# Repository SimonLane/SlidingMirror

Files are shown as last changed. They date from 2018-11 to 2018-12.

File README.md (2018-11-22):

# Sliding Mirror

For use in alternating between two beams in a microscopy setup. A mirror is moved into position with high reposition accuracy. It has been tested on lasers with path lengths ~4.5m and found to allow better repeatability than for example a ThorLabs flip mirror. It also has the advangtage of optionally being automated.
A translation stage is used to provide the linear translation whilst movement is generated by a servo. A spring couples the servo arm to the stage, allowing the stage to be held tight against one end of its range to ensure the same position every time.

Could also be used to add/remove other components e.g. lenses, from optical path where high positional accuracy is needed.

The design comes in two sizes, based around the 13mm and 25mm translation stages available from ThorLabs. 25mm is easier to set-up and allows space for multiple optical components on the stage, whilst 13mm has a smaller footprint. If using the 13mm, then the 'edgeless' mirror design may be useful.

The designs assume mounting on an optical breadboard with 25mm spacing for M6 bolts.

## Bill of Materials

Part | Number | Product Code | Company | Cost (Aprox. GBP)
---|---|---|---|---
Translation Stage 25mm (or 13mm) | 1 | PT1B/M (MT1B/M) | ThorLabs | 161.42 (167.54)
Mirror mount   | 1   | application specific | -  |  -
M6 screw | 1 pack | SH6MS20 | ThorLabs | 6.66
Servo  | 1 | 781-3058 | RSonline | 11.06
Wires  |  1   | 214-0661 |  RS Online   | 14.29
Switch | 1 | 734-7154 | RS Online | 2.33
USB cable   | 1   | 121-6574   | RS Online  |  2.41
Arduino nano (or similar)  |  1  |  1050-1001-ND | Digi-Key  |  16.66
Spring | 1 pack |  2444377 | Farnell | 6.87
Machine screws | 1 pack | 560-596 | RS Online | 2.39

## Assembly
* Print the 3D part using at least 50% infill
* Remove three of the four servo arms and attach to the servo.
* Attach the servo to the base with M3 screws
* Remove the plug from the servo, then solder the wires to the Arduino Nano as shown in the wiring diagram below
    * Red to 5V*
    * Black to Ground
    * Yellow to any PWM (pin D3,5,6,9,10 or 11)
    * Switch wire one to Ground
    * Switch wire two to Digital pin e.g. D4
**The servo can draw 140mA, which is comfortably handled by the arduino and the USB supply from a computer*
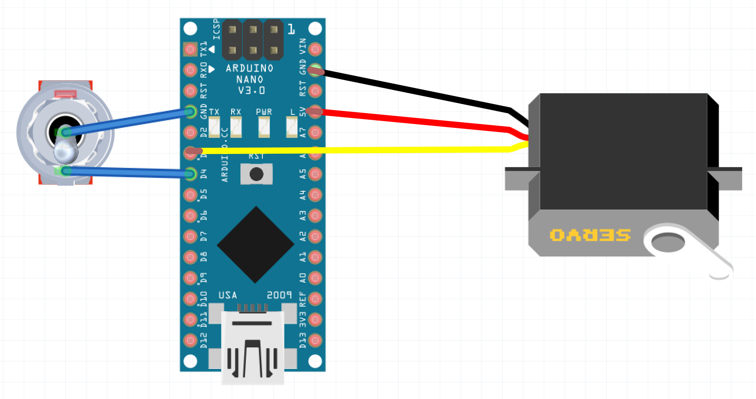
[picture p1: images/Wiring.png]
Wiring Diagram

* Mount the arduino on the side of the servo with hot glue for convenience
* Attach the 3D printed part to the breadboard using an M6 screw. If working along the 90 degree angles of the board then two screws can be added. In the example shown a 45 degree angle is used, and only one screw is added. A second screw hole is provided on the 25mm version to ensure a neat 45 degree angle is made.
* Use an extension spring, bending the ends as needed to connect the stage to the servo arm. The 13mm design has a screw hole that is used as a mount point for the sprnig, whilst the 25mm version has an additional 3D printed part to act as the mount point.
* The switch can be mounted somewhere more convenient for manual adjustment of the position.
* Attatch the USB wire to supply power, and also for automated control.

## Software

The provided arduino code can be uploaded to the board by following the instructions to install the Arduino IDE and upload the script.

The software makes use of the arduino servo library to control the mirror position.

## Use

The software is designed to move the servo arm slowly. Note that quick movements cause impact against the ends of the linear stage and the vibration produced can cause changes to mirror positions over time.

### Manual 
Position is easily changed by toggling the switch
### Automated
Position can be changed over the serial port by sending the commands "/A;" or "/B;" 
The arduino will reply with "/stable;", once the servo has reached the desired position

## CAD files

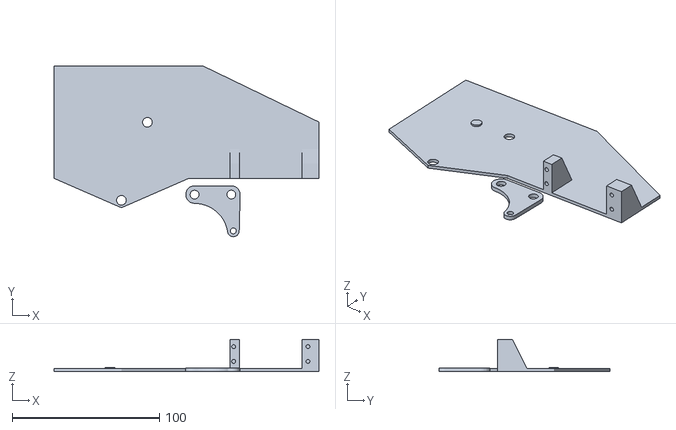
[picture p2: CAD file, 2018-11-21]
SlidingMirror25.stl
180.1 x 115.9 x 22.0

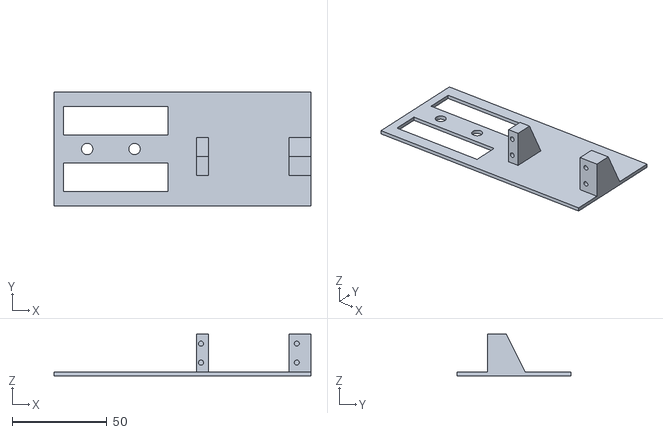
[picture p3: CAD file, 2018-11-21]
SlidingMirror13.stl
135.5 x 60.0 x 22.0

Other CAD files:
SlidingMirror13.skp
SlidingMirror25.skp

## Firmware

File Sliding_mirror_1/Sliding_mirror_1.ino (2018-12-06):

#include <Servo.h>
//~~~~~~~~~~~~~~~~~~~~~~~~~ can edit ~~~~~~~~~~~~~~~~~~~~~~~~~//

int servoPin    = 3;       //pin to which servo has been attached
int switchPin   = 4;       //pin to which stitch has been attached
int servo_pos_0 = 0;       //'off' position
int servo_pos_1 = 160;     //'on' position, calibrate to give slight tension on the spring to ensure repeatable position
int step_time   = 50;      //milliseconds spent on each step, determines servo move speed

//~~~~~~~~~~~~~~~~~~~~~~~~~ don't edit ~~~~~~~~~~~~~~~~~~~~~~~~~//

Servo servo;
void setup() {
  servo.attach(servoPin); 
  pinMode(switchPin,INPUT_PULLUP);
  Serial.begin(115200);
}


int d_servo_position = servo_pos_1;
int c_servo_position = 80;
long unsigned int prev_time = 0;
bool stable = false;

void update_servo_position(){
  long unsigned int current_time = millis();
  if(current_time > prev_time + 50){
    prev_time = current_time;
    if(d_servo_position > c_servo_position) {
      c_servo_position = c_servo_position + 1;
      servo.write(c_servo_position);
      stable = false;
      }
    if(d_servo_position < c_servo_position) { 
      c_servo_position = c_servo_position - 1; 
      servo.write(c_servo_position);
      stable = false;
      }
    if(d_servo_position == c_servo_position && not stable){
      stable = true;
      Serial.println("/stable;");
    }
  }
}

// serial commands
String device = "";
String command1 = "";
int serial_part = 0;

void check_serial(){   
  char rc;
  while (Serial.available()) {
   rc = Serial.read();
   if      (rc == 47)         {serial_part = 1; device = "";command1 = "";}   // '/' char
   else if (rc == 46)         {serial_part += 1;}                             // '.' char
   else if (rc == 59)         {respond(device,command1); serial_part = 0;}    // ';' char
   else if (serial_part == 1) {device   += rc;}
   else if (serial_part == 2) {command1 += rc;}
 }
}

void respond(String device,String command1) {
    if(device == "A")         {d_servo_position = servo_pos_1;}
    if(device == "B")         {d_servo_position = servo_pos_0;}
    if(device == "hello")     {Serial.println("Sliding Mirror");}
  }

int prev_switch_position  = 0;

void check_switch(){
  if(digitalRead(switchPin) != prev_switch_position) { // the switch has been moved
    prev_switch_position = digitalRead(switchPin);
    if      (d_servo_position == servo_pos_0)  {d_servo_position = servo_pos_1;}  //toggle position
    else if (d_servo_position == servo_pos_1)  {d_servo_position = servo_pos_0;}  //toggle position
  }
}

void loop() {
  update_servo_position();
  check_switch();
  check_serial();
}

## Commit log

2018-11-21 design files added
    [SlidingMirror13.skp, SlidingMirror13.stl, SlidingMirror25.skp, SlidingMirror25.stl]
2018-11-21 wiring diagram added
2018-11-21 new wiring diagram for nano
2018-11-22 Added serial control to servo
